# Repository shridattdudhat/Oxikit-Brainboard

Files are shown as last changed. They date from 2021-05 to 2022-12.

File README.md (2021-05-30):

# Oxikit-Brainboard

An Open Source Oxygen Concentrator Brain Board

Following are details of each directory:

- **BOM** : Bill Of Material for BrainBoard
- **Firmware** : Firmware to use with BrainBoard. It has two different firmware folder. 
  - Particle Electron Firmware
  - ESP32 TTGO T-Call firmware
- **gerberFiles** : You can download the zip and give for production.
- **images** : It has all the 3D images of BrainBoard
- **kicadProject** : It cotains all the files of Kicad Project. One can install latest Kicad nightly build and run the project to modify it. 
- **schematic** : Schematic file of the PCB

Some Kicad generated 3D images:

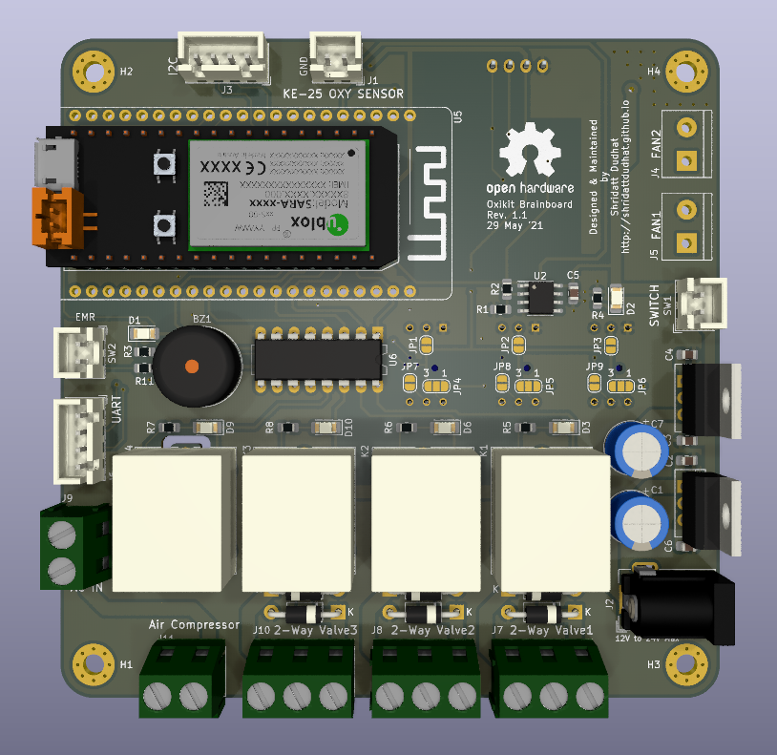
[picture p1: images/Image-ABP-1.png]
Front Side

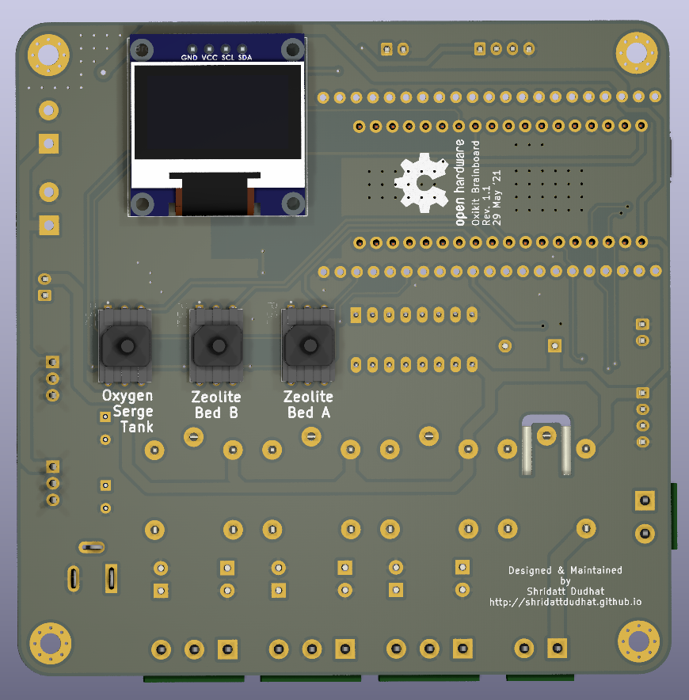
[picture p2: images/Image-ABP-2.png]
Back Side

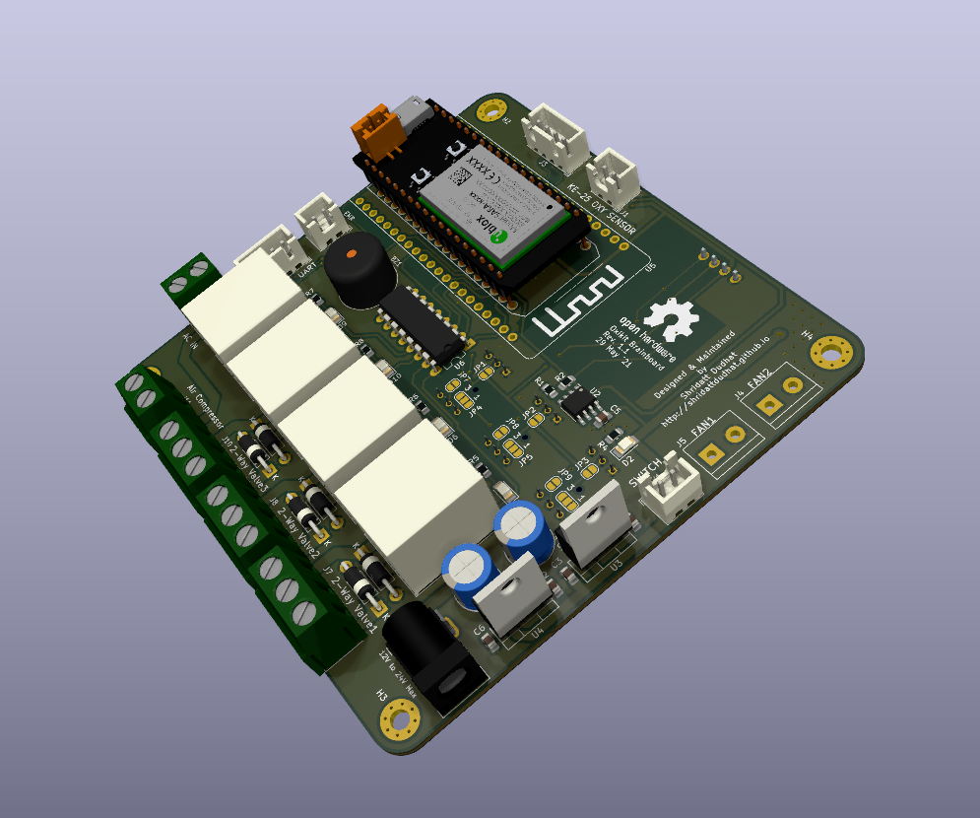
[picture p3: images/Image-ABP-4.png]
Side View


First prototypes of BrainBoard:

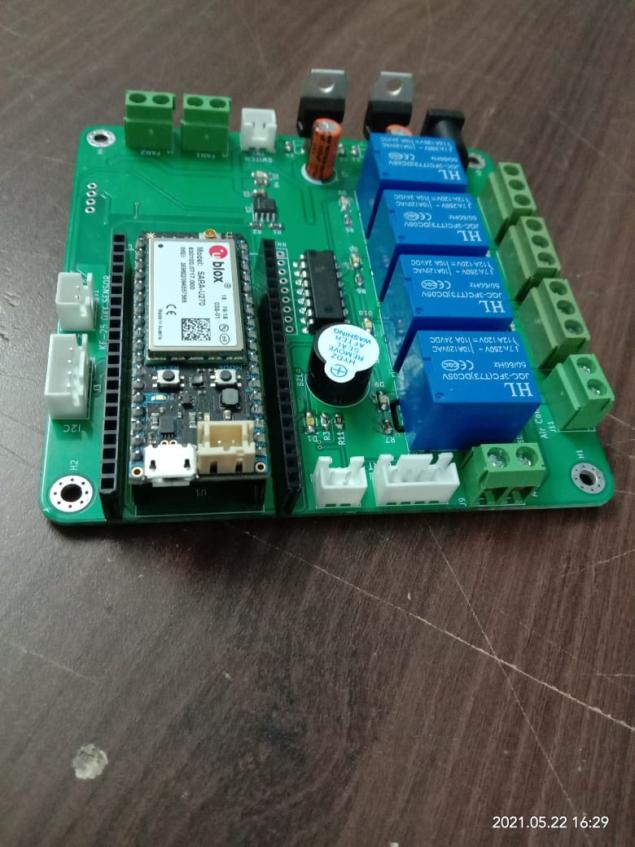
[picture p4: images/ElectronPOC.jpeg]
Particle electron

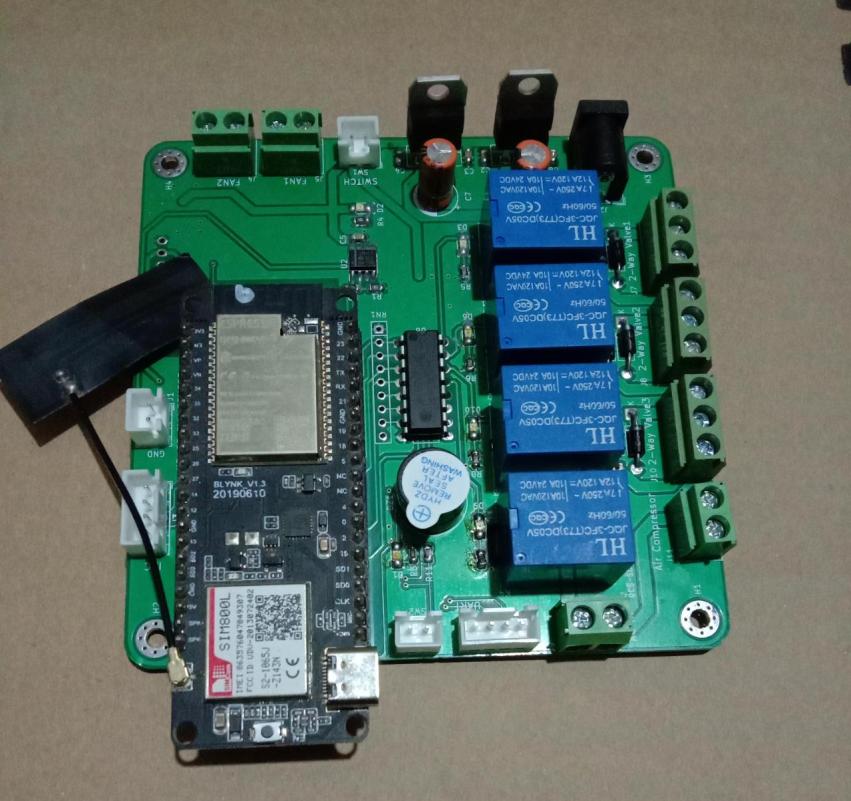
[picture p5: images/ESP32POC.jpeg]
EPS32


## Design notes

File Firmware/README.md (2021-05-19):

Will be uploading firmware for Electron and ESP32 soon.

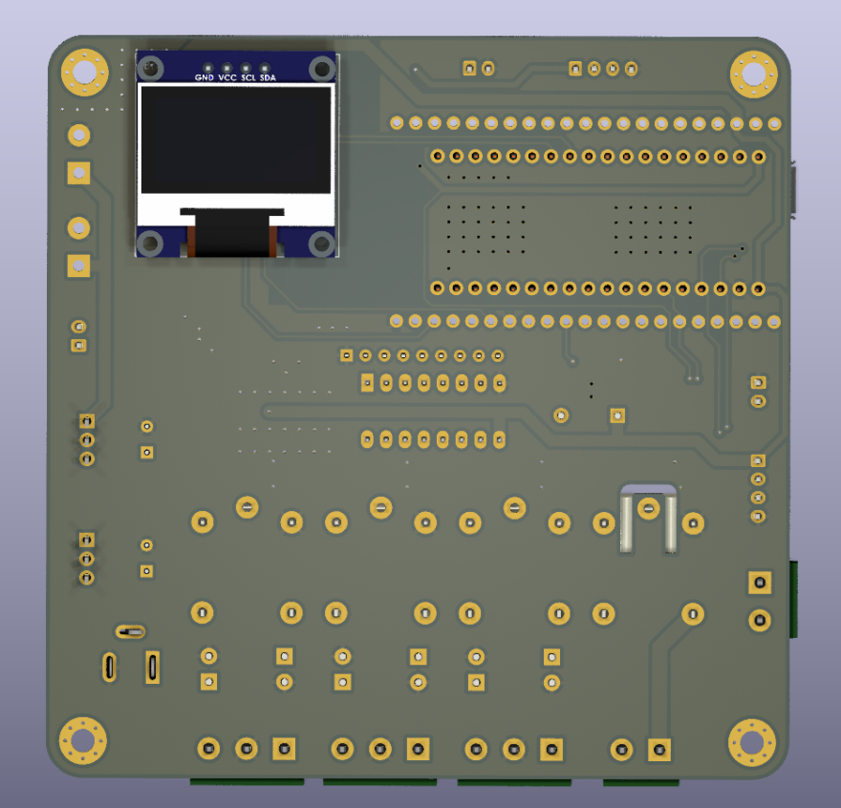
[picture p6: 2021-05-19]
images/back.png

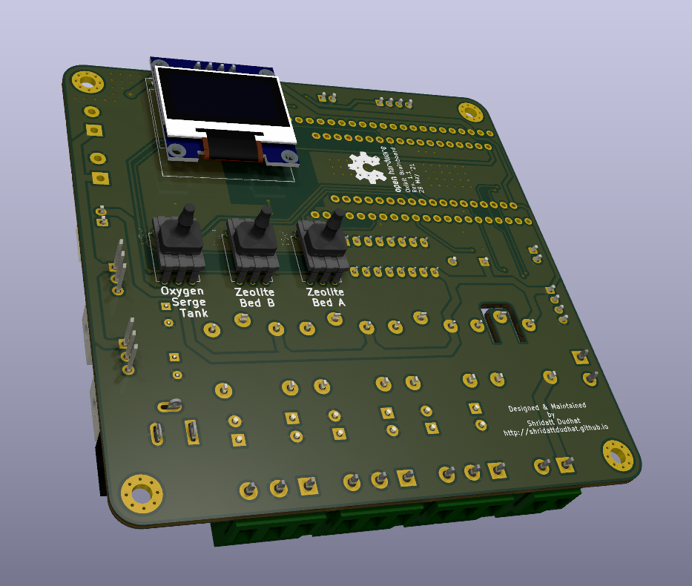
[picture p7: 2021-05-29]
images/Image-ABP-3.png

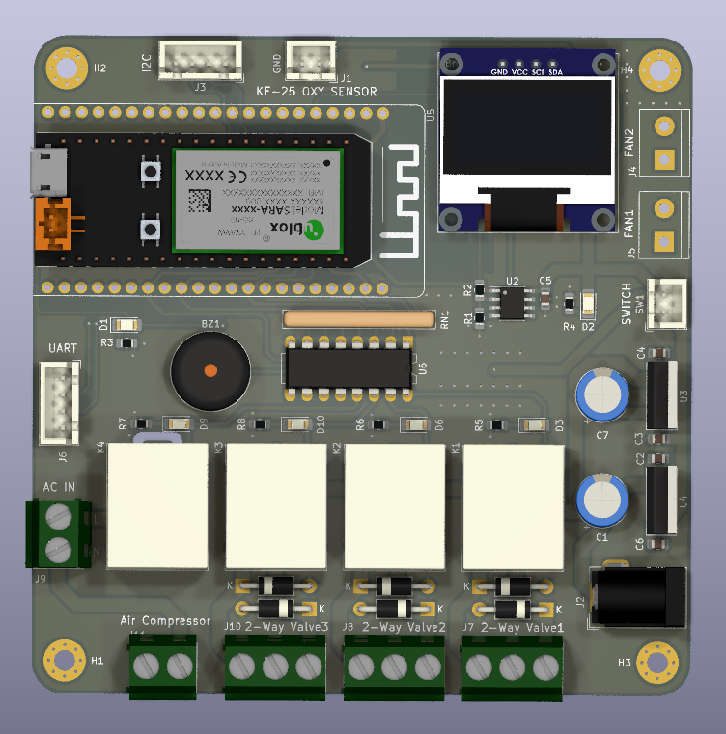
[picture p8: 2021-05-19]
images/front.png

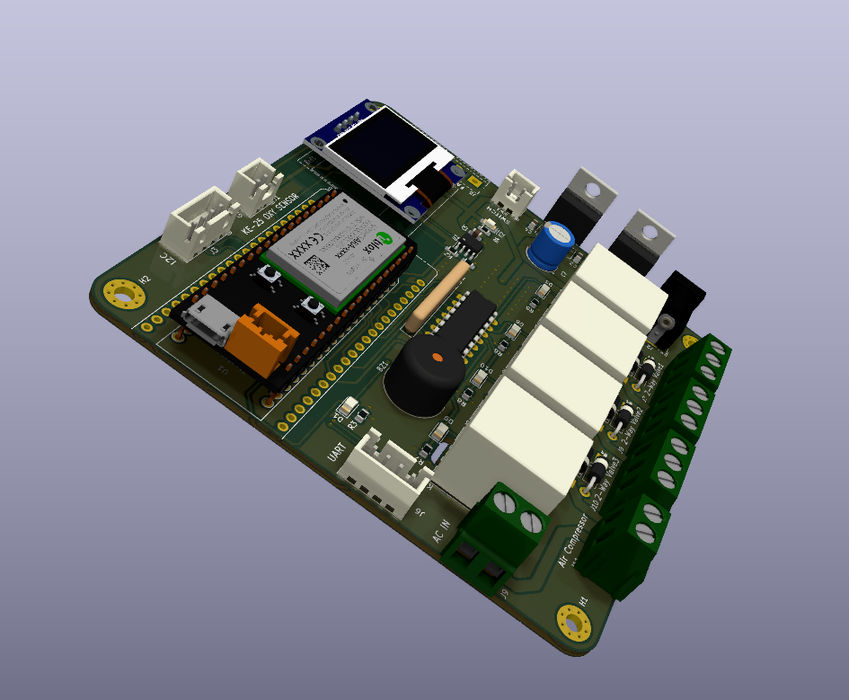
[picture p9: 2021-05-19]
images/sideView.png

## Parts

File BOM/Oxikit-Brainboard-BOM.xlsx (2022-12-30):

Sr. No. | Designator | Component value | Manufacturer Part Number | Qty per PCB | Package / Case | Per Component | Per PCB | Description | Ref Link (Local Purchase)
1 | Brd1 | SSD1306 | * | 1 | SSD1306:128x64OLED | 300 | 300 | I2C OLED Display | https://www.sunrobotics.in/shop/product/7375-oled-0-96-inch-i2c-display-module-4-pin-generic-3930
2 | BZ1 | Buzzer | * | 1 | Buzzer_Beeper:Buzzer_12x9.5RM7.6 | 15 | 15 | Electromagnetic Active Buzzer 5V | https://www.sunrom.com/p/electromagnetic-active-buzzer-5v
3 | C1, C7 | 220uF | MCGPR16V227M6.3X11 | 2 | Capacitor_THT:CP_Radial_D8.0mm_P3.50mm | 3 | 6 | Electrolytic Capacitor, 220 µF, 16 V, MCGPR Series, ± 20%, Radial Leaded, 2000 hours @ 85°C
4 | C2, C3, C4, C6 | 1uF | MC0805F105Z500CT | 4 | Capacitor_SMD:C_0805_2012Metric_Pad1.18x1.45mm_HandSolder | 2 | 8 | 1 µF, 50 V, 0805 [2012 Metric] | https://www.sunrom.com/p/1uf-105-0805-2012-metric
5 | C5 | 100nF | MC0805B104M500CT | 1 | Capacitor_SMD:C_0805_2012Metric_Pad1.18x1.45mm_HandSolder | 1 | 1 | 0.1 µF, 50 V, 0805 [2012 Metric], ± 20%, X7R | https://www.sunrom.com/p/100nf-104-0805-2012-metric
6 | D1, D2, D3, D6, D9, D10 | LED | * | 6 | LED_SMD:LED_1206_3216Metric_Pad1.42x1.75mm_HandSolder | 1 | 6 | Red SMD LED 1206 | https://www.sunrom.com/p/red-smd-led-1206
7 | D4, D5, D7, D8, D11, D12 | 1N4007 | 1N4007 | 6 | Diode_THT:D_DO-41_SOD81_P10.16mm_Horizontal | 1.5 | 9 | DIODE, STANDARD RECOVERY, 1A, 1KV, DO-41 | https://www.sunrom.com/p/1n4007-1a-diode
8 | J1 | OXY-Sensor | * | 1 | Connector_JST:JST_XH_B2B-XH-A_1x02_P2.50mm_Vertical | 1.5 | 1.5 | JST 2 Pin 2.54mm Pitch | https://www.sunrom.com/p/2-pin-jst-xh-25mm-top-entry-header
9 | J2 | Jack-DC | * | 1 | Connector_BarrelJack:BarrelJack_Wuerth_6941xx301002 | 13 | 13 | DC Socket - 1mm legs - Suitable for 5.5x2.1mm DC Pins | https://www.sunrom.com/p/dc-socket---1mm-legs---suitable-for-55x21mm-dc-pins
10 | J3, J6 | UART, I2C | * | 2 | Connector_JST:JST_XH_B4B-XH-A_1x04_P2.50mm_Vertical |  |  | 4 pin JST XH 2.5mm Top Entry Header | https://www.sunrom.com/p/4-pin-jst-xh-25mm-top-entry-header
11 | J4, J5, J9, J11 | Fan1 | * | 4 | TerminalBlock:TerminalBlock_bornier-2_P5.08mm | 7 | 28 | 2P 5mm 10A Screw Terminal Light | https://www.sunrom.com/p/2p-5mm-10a-screw-terminal-light
12 | J7, J8, J10 | Valve1 | * | 3 | TerminalBlock:TerminalBlock_bornier-3_P5.08mm | 11 | 33 | 3P 5mm 10A Screw Terminal Light | https://www.sunrom.com/p/3p-5mm-10a-screw-terminal-light
13 | K1, K2, K3, K4 | FINDER-36.11 | * | 4 | Relay_THT:Relay_SPDT_Finder_36.11 | 24 | 100 | Relay 5V - PCB Mount | https://www.sunrom.com/p/relay-5v-pcb-mount
14 | R1, R4, R5, R6, R7, R8, R9, R10, R11 | 1K | MCWR08X1001FTL | 9 | Resistor_SMD:R_0805_2012Metric_Pad1.20x1.40mm_HandSolder | 0.5 | 5 | 1 kohm, ± 1%, 125 mW, 0805 [2012 Metric] | https://www.sunrom.com/p/1k-1-0805-pack-of-100
15 | R2 | 10K | MCWR08X1002FTL | 1 | Resistor_SMD:R_0805_2012Metric_Pad1.20x1.40mm_HandSolder | 0.5 | 0.5 | 10 kohm, ± 1%, 125 mW, 0805 [2012 Metric] | https://www.sunrom.com/p/10k-1-0805-pack-of-100
16 | R3 | 330R | MCWR08X3300FTL | 1 | Resistor_SMD:R_0805_2012Metric_Pad1.20x1.40mm_HandSolder | 0.5 | 0.5 | 330 ohm, ± 1%, 125 mW, 0805 [2012 Metric] | https://www.sunrom.com/m/6867
18 | SW1, SW2 | Switch | * | 2 | Connector_JST:JST_XH_B2B-XH-A_1x02_P2.50mm_Vertical |  |  | JST 2 Pin 2.54mm Pitch | https://www.sunrom.com/p/2-pin-jst-xh-25mm-top-entry-header
19 | U1 | Electron |  | 1 | particle:electron
20 | U2 | LM358 | LM358EDR2G | 1 | Package_SO:SOIC-8_3.9x4.9mm_P1.27mm | 13 | 13 | Operational Amplifier, 2 Amplifier, 1 MHz, 0.6 V/µs, 3V to 32V, SOIC, 8 Pins
21 | U3, U4 | LM7805_TO220 | L7805CV | 2 | Package_TO_SOT_THT:TO-220-3_Vertical | 15 | 30 | Linear Voltage Regulator, 7805, Fixed, Positive, 10V To 35V In, 5V And 1.5A Out, TO-220-3
22 | U5 | TTGO-TCALL-SIM800 |  | 1 | TTGO-TCALL-SIM800:TTGO-TCALL-SIM800
23 | U6 | ULN2003A | ULN2003AN . | 1 | Package_DIP:DIP-16_W7.62mm_LongPads | 21 | 21 | Bipolar Transistor Array, NPN, 50 V, 500 mA, 25 W, 600 hFE, DIP | https://www.sunrom.com/p/uln2003a-dip
 |  |  | * Please Check links in last column

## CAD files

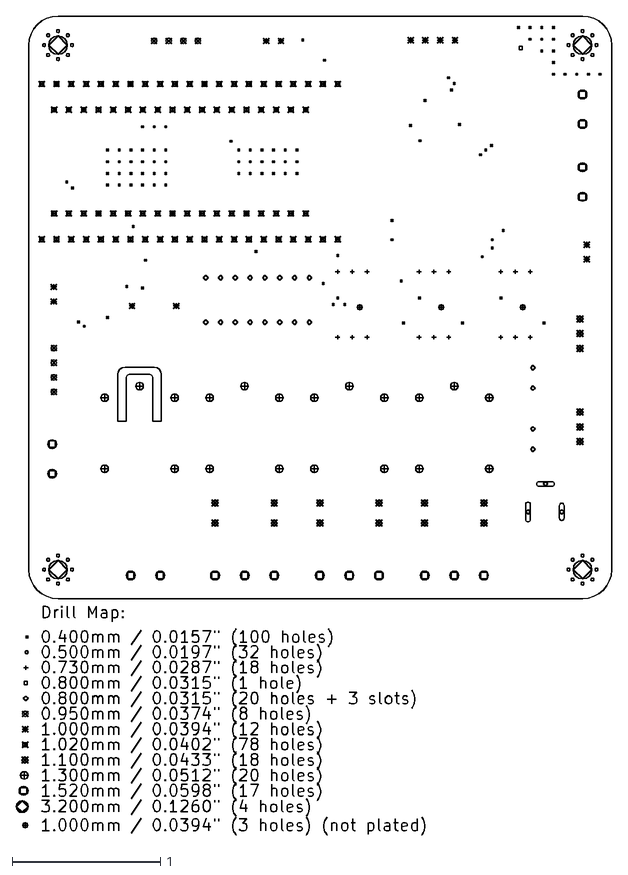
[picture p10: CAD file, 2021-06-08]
kicadProject/OxiKit-Brainboard_v1-GERBER/OxiKit-Brainboard_v1-drl_map.dxf
4.02 x 5.53

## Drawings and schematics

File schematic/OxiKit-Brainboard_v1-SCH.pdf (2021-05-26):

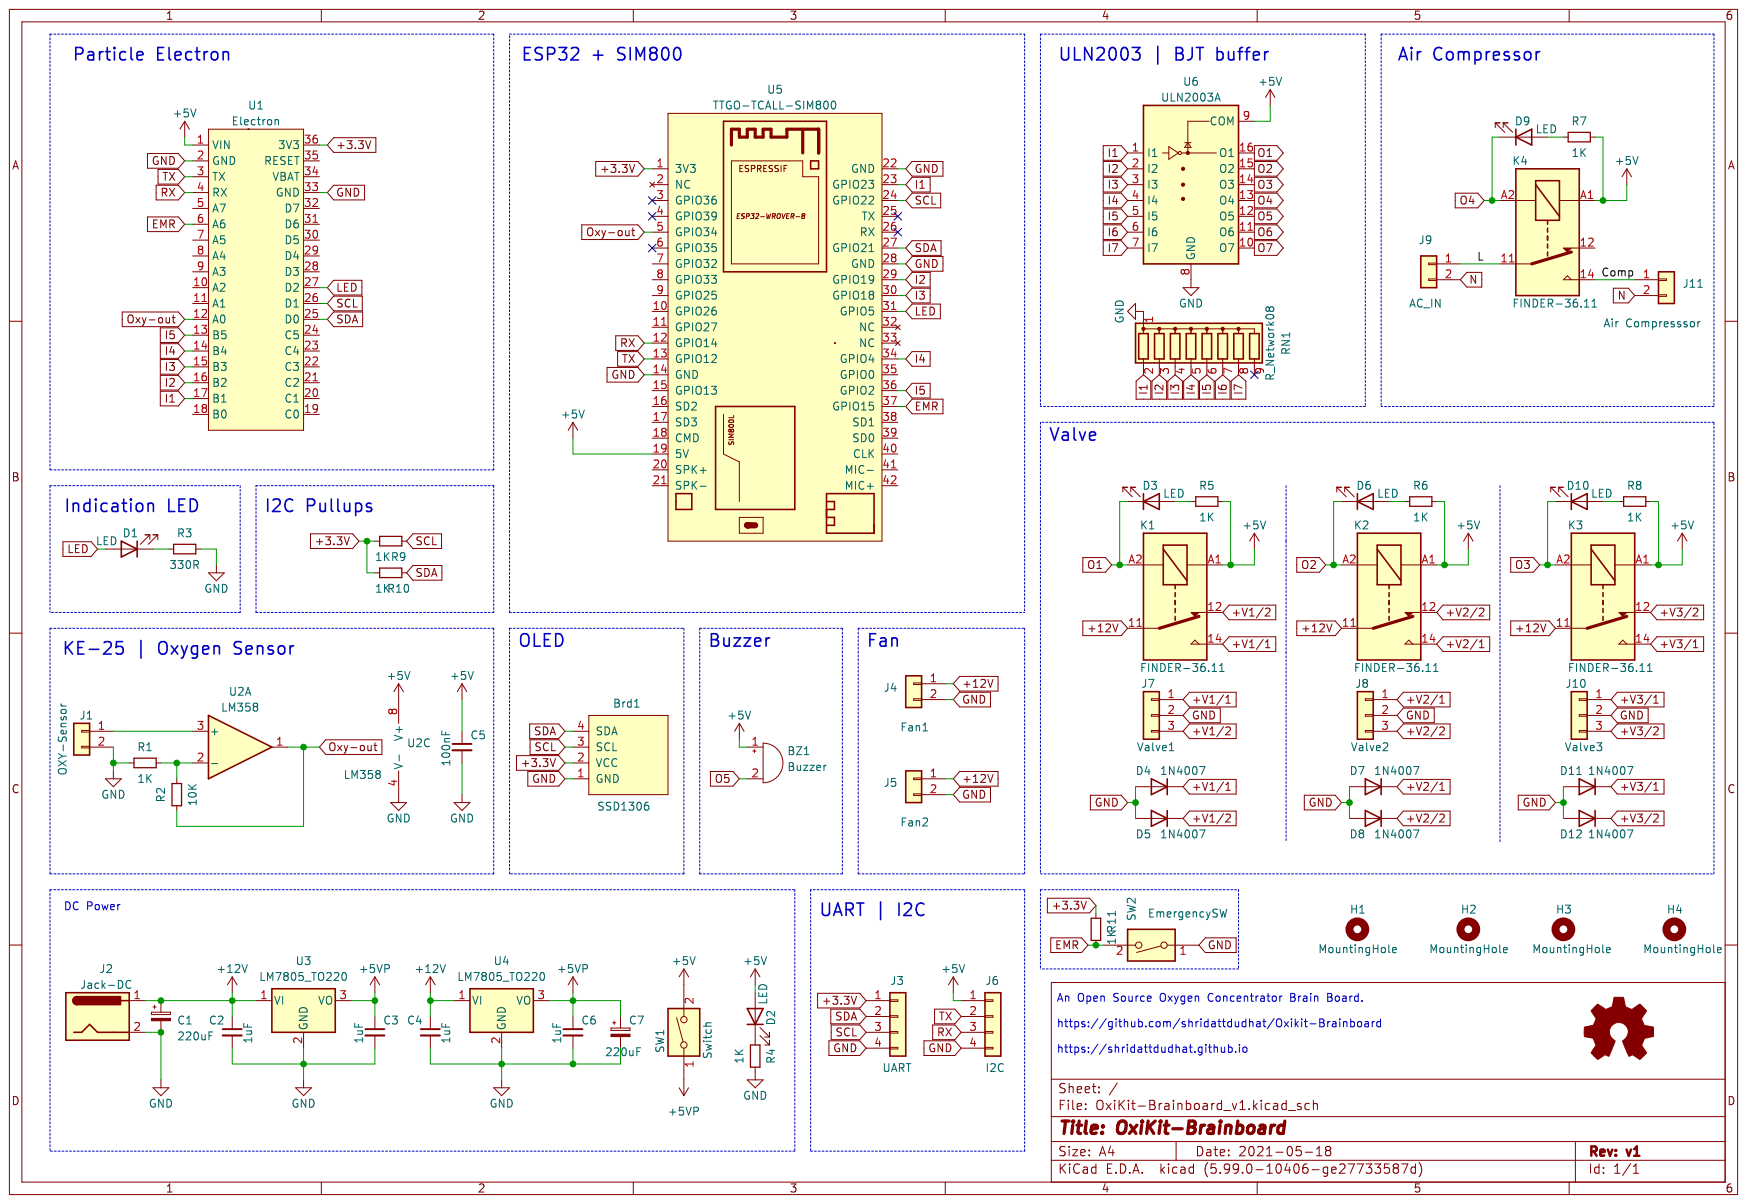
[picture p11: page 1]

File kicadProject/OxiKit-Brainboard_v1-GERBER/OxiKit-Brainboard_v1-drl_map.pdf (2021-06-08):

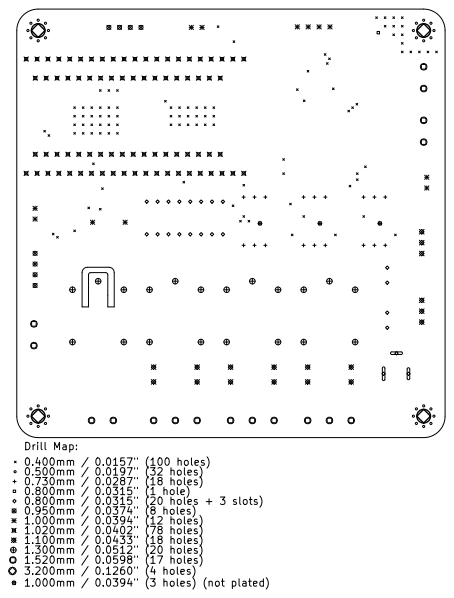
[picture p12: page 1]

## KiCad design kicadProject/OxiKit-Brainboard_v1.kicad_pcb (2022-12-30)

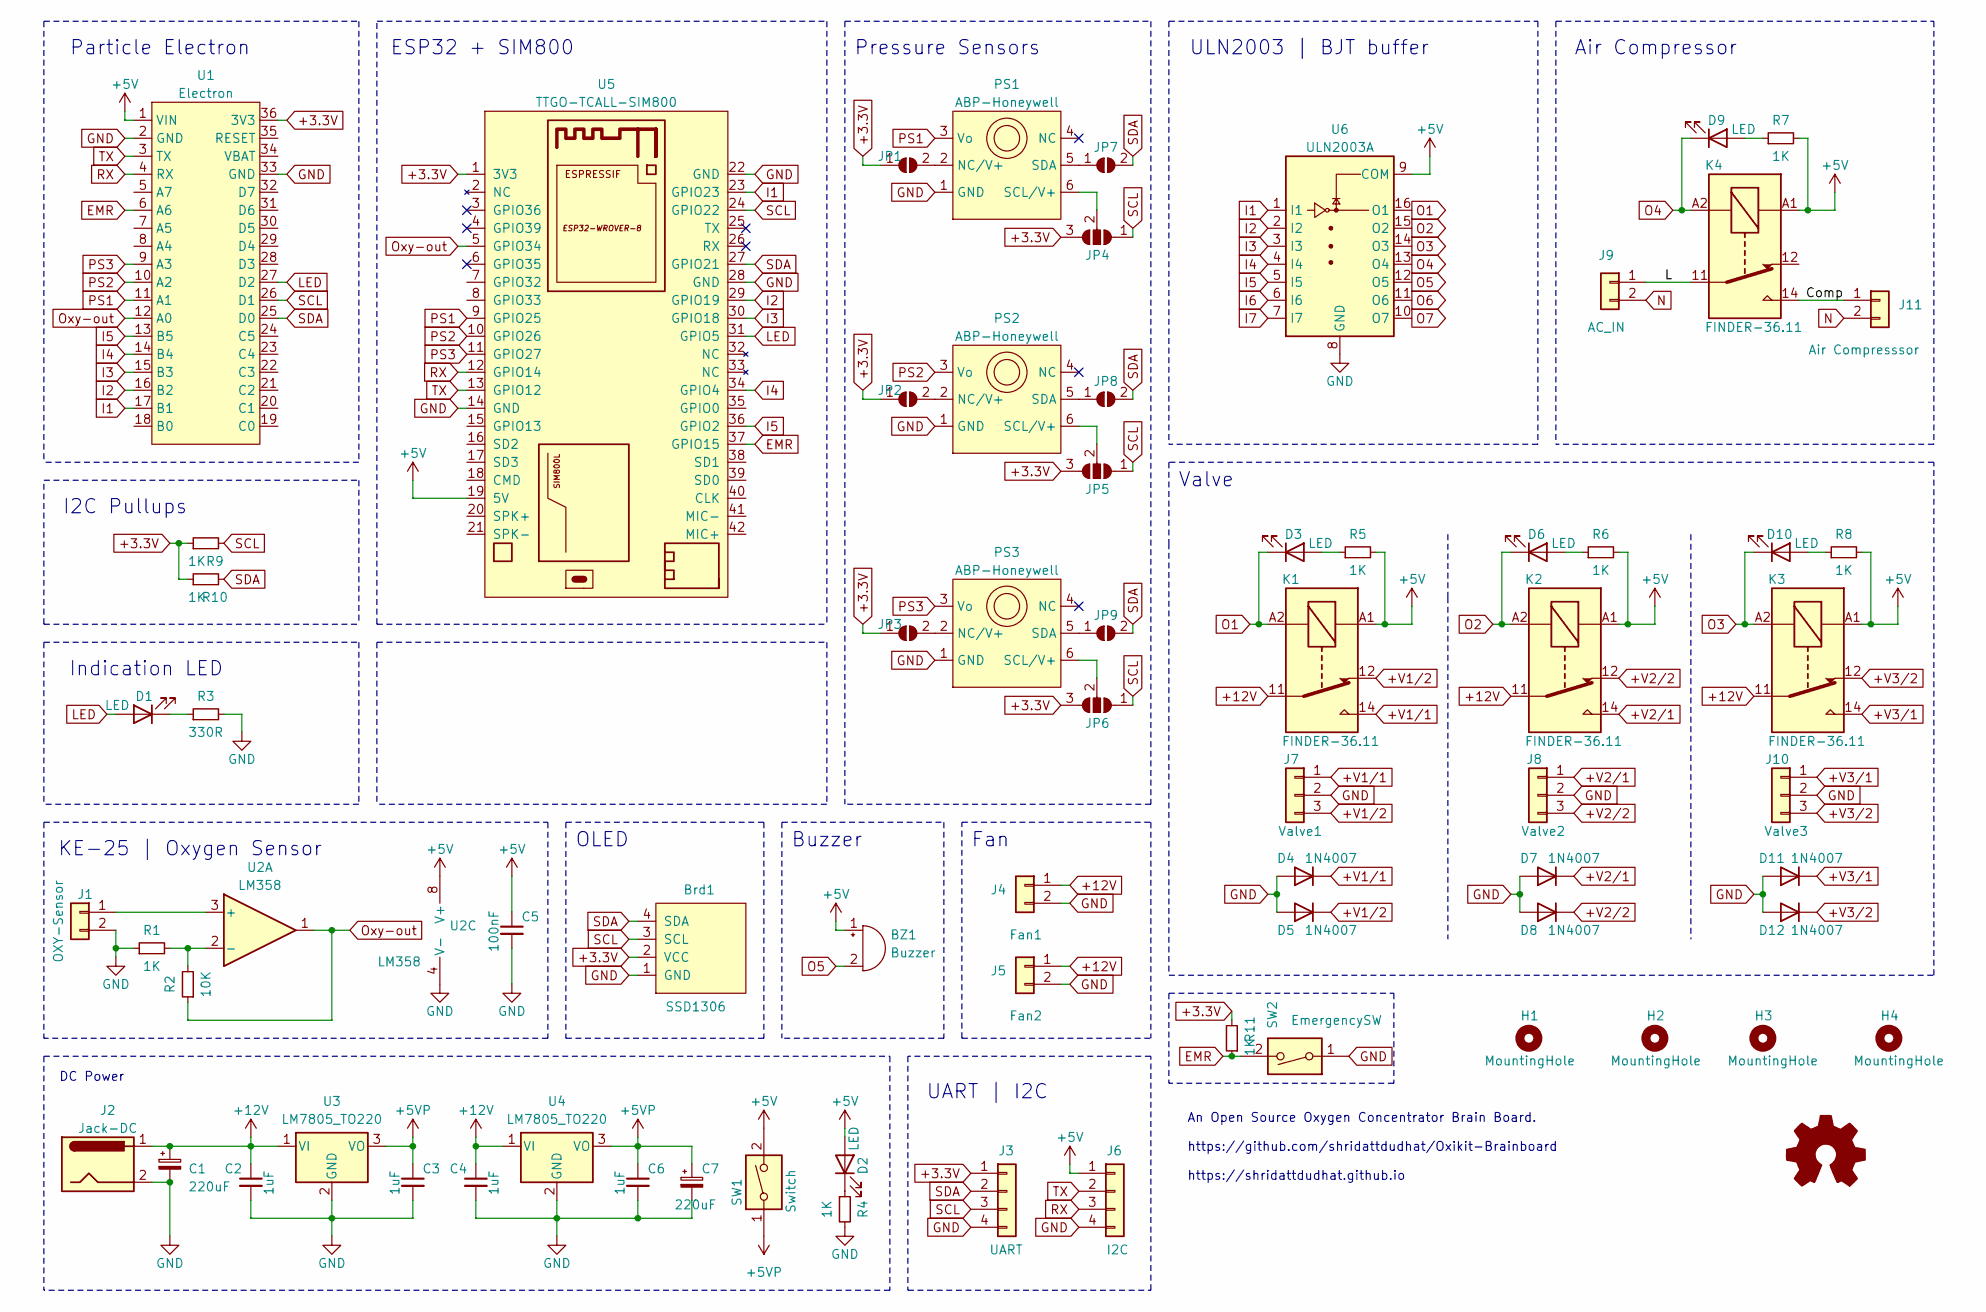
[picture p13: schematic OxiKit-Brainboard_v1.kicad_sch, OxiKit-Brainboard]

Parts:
BZ1: Buzzer; Buzzer_12x9.5RM7.6
Brd1: SSD1306; 128x64OLED
C1, C7: 220uF; CP_Radial_D8.0mm_P3.50mm
C2, C3, C4, C6: 1uF; C_0805_2012Metric_Pad1.18x1.45mm_HandSolder
C5: 100nF; C_0805_2012Metric_Pad1.18x1.45mm_HandSolder
D1, D2, D3, D6, D9, D10: LED; LED_1206_3216Metric_Pad1.42x1.75mm_HandSolder
D4, D5, D7, D8, D11, D12: 1N4007; D_DO-41_SOD81_P10.16mm_Horizontal
H1, H2, H3, H4: MountingHole; MountingHole_3.2mm_M3_Pad_Via
J1: OXY-Sensor; JST_XH_B2B-XH-A_1x02_P2.50mm_Vertical
J2: Jack-DC; BarrelJack_Wuerth_6941xx301002
J3: UART; JST_XH_B4B-XH-A_1x04_P2.50mm_Vertical
J4: Fan1; TerminalBlock_bornier-2_P5.08mm
J5: Fan2; TerminalBlock_bornier-2_P5.08mm
J6: I2C; JST_XH_B4B-XH-A_1x04_P2.50mm_Vertical
J7: Valve1; TerminalBlock_bornier-3_P5.08mm
J8: Valve2; TerminalBlock_bornier-3_P5.08mm
J9: AC_IN; TerminalBlock_bornier-2_P5.08mm
J10: Valve3; TerminalBlock_bornier-3_P5.08mm
J11: Air Compresssor; TerminalBlock_bornier-2_P5.08mm
JP1, JP2, JP3, JP7, JP8, JP9: SolderJumper_2_Open; SolderJumper-2_P1.3mm_Open_RoundedPad1.0x1.5mm
JP4, JP5, JP6: SolderJumper_3_Open; SolderJumper-3_P1.3mm_Open_RoundedPad1.0x1.5mm_NumberLabels
K1, K2, K3, K4: FINDER-36.11; Relay_SPDT_Finder_36.11
PS1, PS2, PS3: ABP-Honeywell; ABP-Series-Pressure
R1, R4, R5, R6, R7, R8, R9, R10, R11: 1K; R_0805_2012Metric_Pad1.20x1.40mm_HandSolder
R2: 10K; R_0805_2012Metric_Pad1.20x1.40mm_HandSolder
R3: 330R; R_0805_2012Metric_Pad1.20x1.40mm_HandSolder
SW1: Switch; JST_XH_B2B-XH-A_1x02_P2.50mm_Vertical
SW2: EmergencySW; JST_XH_B2B-XH-A_1x02_P2.50mm_Vertical
U1: Electron; electron
U2: LM358
U3, U4: LM7805_TO220; TO-220-3_Vertical
U5: TTGO-TCALL-SIM800
U6: ULN2003A; DIP-16_W7.62mm_LongPads

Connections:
+3.3V: Brd1.2 (VCC), J3.1, JP1.1 (A), JP2.1 (A), JP3.1 (A), JP4.3 (B), JP5.3 (B), JP6.3 (B), R9.1, R10.1, R11.2, U1.36 (3V3), U5.1 (3V3)
+5V: BZ1.1 (-), C5.1, D2.2 (A), J6.1, K1.A1, K2.A1, K3.A1, K4.A1, R5.2, R6.2, R7.2, R8.2, SW1.2, U1.1 (VIN), U2.8 (V+), U5.19 (5V), U6.9 (COM)
+5VP: C3.1, C6.1, C7.1, SW1.1, U3.3 (VO), U4.3 (VO)
+12V: C1.1, C2.1, C4.1, J2.1, J4.1, J5.1, K1.11, K2.11, K3.11, U3.1 (VI), U4.1 (VI)
+V1/1: D4.1 (K), J7.1, K1.14
+V1/2: D5.1 (K), J7.3, K1.12
+V2/1: D7.1 (K), J8.1, K2.14
+V2/2: D8.1 (K), J8.3, K2.12
+V3/1: D11.1 (K), J10.1, K3.14
+V3/2: D12.1 (K), J10.3, K3.12
/Comp: J11.1, K4.14
/L: J9.1, K4.11
EMR: R11.1, SW2.2, U1.6 (A6), U5.37 (GPIO15)
GND: Brd1.1 (GND), C1.2, C2.2, C3.2, C4.2, C5.2, C6.2, C7.2, D4.2 (A), D5.2 (A), D7.2 (A), D8.2 (A), D11.2 (A), D12.2 (A), J1.2, J2.2, J3.4, J4.2, J5.2, J6.4, J7.2, J8.2, J10.2, PS1.1 (GND), PS2.1 (GND), PS3.1 (GND), R1.1, R3.2, R4.2, SW2.1, U1.2 (GND), U1.33 (GND), U2.4 (V-), U3.2 (GND), U4.2 (GND), U5.14 (GND), U5.22 (GND), U5.28 (GND), U6.8 (GND)
I1: U1.17 (B1), U5.23 (GPIO23), U6.1 (I1)
I2: U1.16 (B2), U5.29 (GPIO19), U6.2 (I2)
I3: U1.15 (B3), U5.30 (GPIO18), U6.3 (I3)
I4: U1.14 (B4), U5.34 (GPIO4), U6.4 (I4)
I5: U1.13 (B5), U5.36 (GPIO2), U6.5 (I5)
I6: U6.6 (I6)
I7: U6.7 (I7)
LED: D1.2 (A), U1.27 (D2), U5.31 (GPIO5)
N: J9.2, J11.2
unnamed: D1.1 (K), R3.1
unnamed: D2.1 (K), R4.1
unnamed: D3.2 (A), R5.1
unnamed: D6.2 (A), R6.1
unnamed: D9.2 (A), R7.1
unnamed: D10.2 (A), R8.1
unnamed: J1.1, U2.3 (+)
unnamed: JP1.2 (B), PS1.2 (NC/V+)
unnamed: JP2.2 (B), PS2.2 (NC/V+)
unnamed: JP3.2 (B), PS3.2 (NC/V+)
unnamed: JP4.2 (C), PS1.6 (SCL/V+)
unnamed: JP5.2 (C), PS2.6 (SCL/V+)
unnamed: JP6.2 (C), PS3.6 (SCL/V+)
unnamed: JP7.1 (A), PS1.5 (SDA)
unnamed: JP8.1 (A), PS2.5 (SDA)
unnamed: JP9.1 (A), PS3.5 (SDA)
unnamed: R1.2, R2.2, U2.2 (-)
O1: D3.1 (K), K1.A2, U6.16 (O1)
O2: D6.1 (K), K2.A2, U6.15 (O2)
O3: D10.1 (K), K3.A2, U6.14 (O3)
O4: D9.1 (K), K4.A2, U6.13 (O4)
O5: BZ1.2 (+), U6.12 (O5)
O6: U6.11 (O6)
O7: U6.10 (O7)
Oxy-out: R2.1, U1.12 (A0), U2.1, U5.5 (GPIO34)
PS1: PS1.3 (Vo), U1.11 (A1), U5.9 (GPIO25)
PS2: PS2.3 (Vo), U1.10 (A2), U5.10 (GPIO26)
PS3: PS3.3 (Vo), U1.9 (A3), U5.11 (GPIO27)
RX: J6.3, U1.4 (RX), U5.12 (GPIO14)
SCL: Brd1.3 (SCL), J3.3, JP4.1 (A), JP5.1 (A), JP6.1 (A), R9.2, U1.26 (D1), U5.24 (GPIO22)
SDA: Brd1.4 (SDA), J3.2, JP7.2 (B), JP8.2 (B), JP9.2 (B), R10.2, U1.25 (D0), U5.27 (GPIO21)
TX: J6.2, U1.3 (TX), U5.13 (GPIO12)

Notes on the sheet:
DC Power
I2C Pullups
Indication LED
Particle Electron
KE-25 | Oxygen Sensor
ESP32 + SIM800
OLED
Buzzer
Pressure Sensors
UART | I2C
Fan
Valve
An Open Source Oxygen Concentrator Brain Board. https://github.com/shridattdudhat/Oxikit-Brainboard https://shridattdudhat.github.io
ULN2003 | BJT buffer
Air Compressor

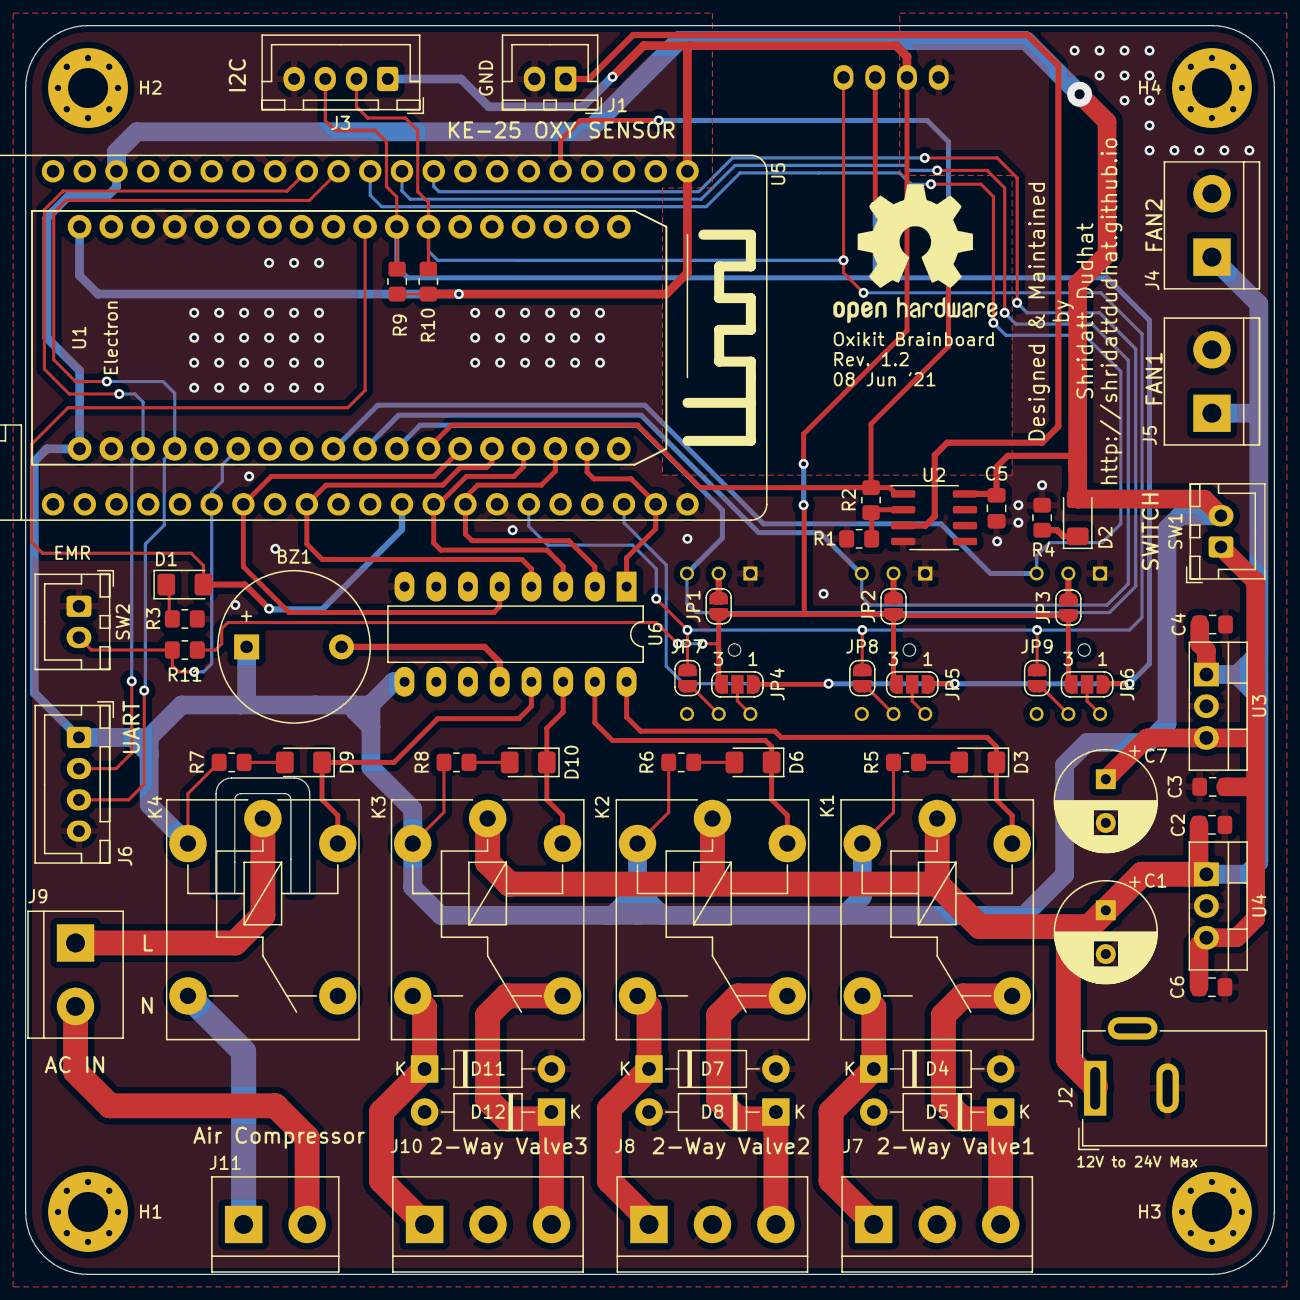
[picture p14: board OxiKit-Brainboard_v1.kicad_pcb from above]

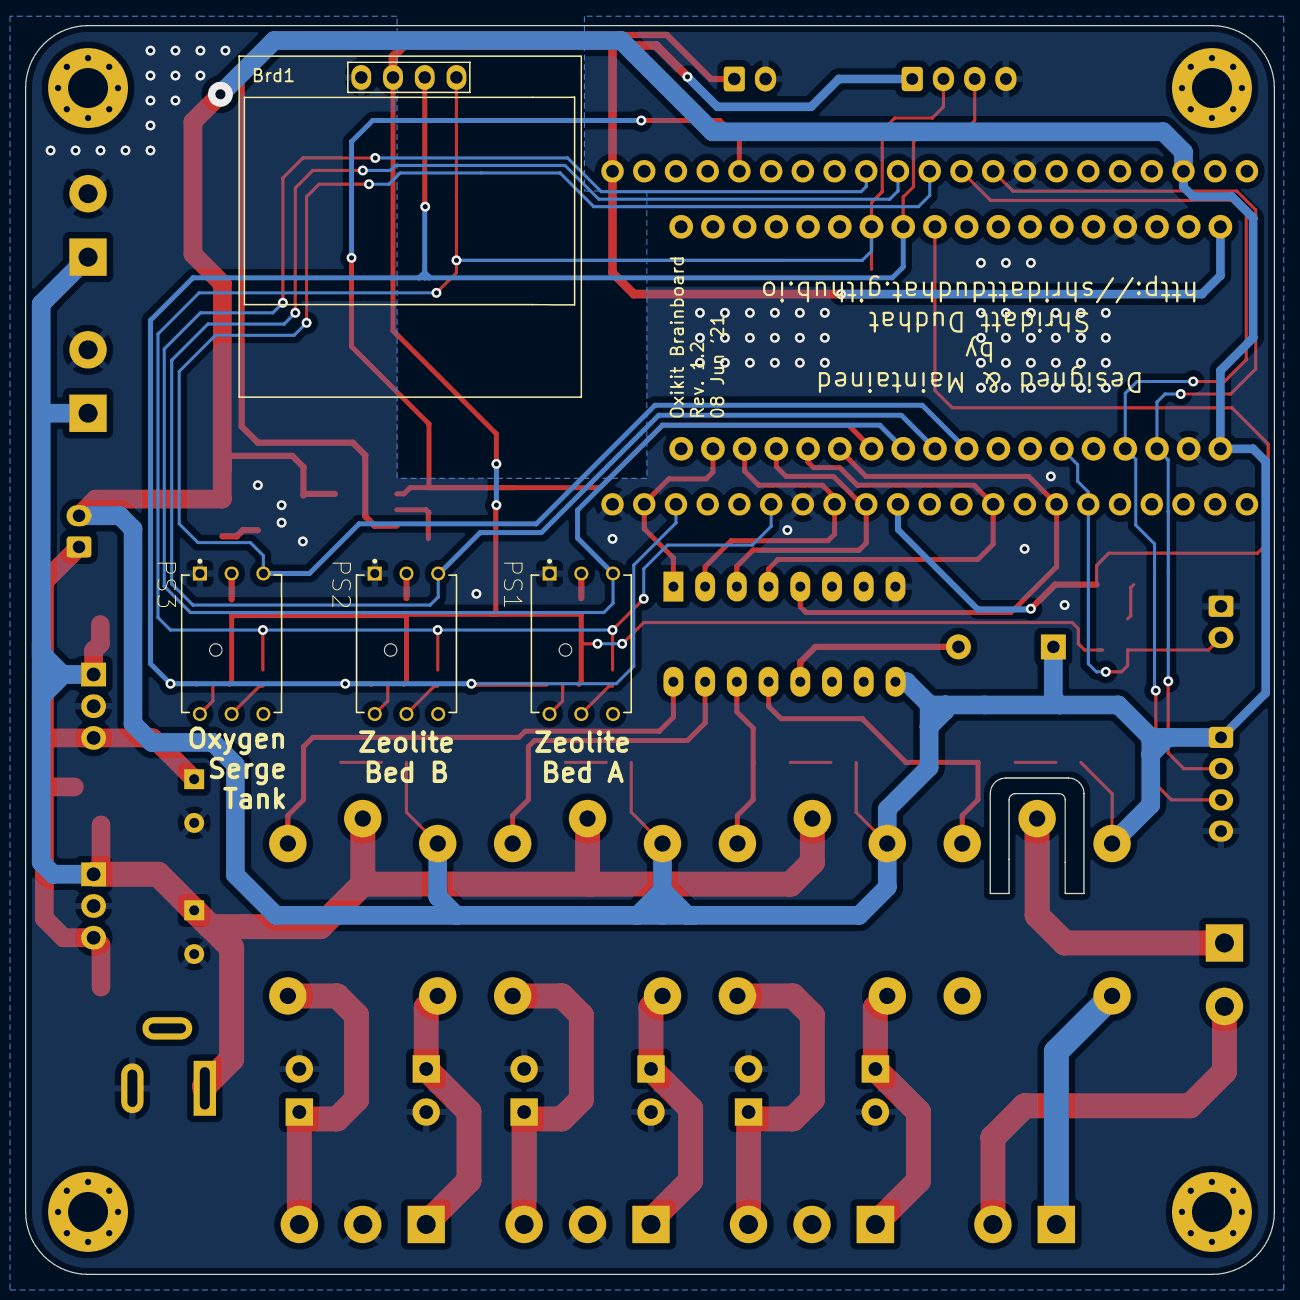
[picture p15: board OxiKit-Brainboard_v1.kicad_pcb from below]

Board: 2 copper layers, 100.0 x 100.0 mm, 71 parts (4 on the bottom side), 51 nets.

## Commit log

2021-05-18 Initial Schematic Commit | Relays, Buzzer, OxySensor, Power Supply, OLED
    [OxiKit-Brainboard_v1.kicad_pcb, OxiKit-Brainboard_v1.kicad_sch]
2021-05-19 Component Placement - L1
    [OxiKit-Brainboard_v1.kicad_pcb, OxiKit-Brainboard_v1.kicad_sch]
2021-05-19 Final routing
    [OxiKit-Brainboard_v1-B_Cu.gbr, OxiKit-Brainboard_v1-B_Mask.gbr, OxiKit-Brainboard_v1-B_Paste.gbr, OxiKit-Brainboard_v1-B_Silkscreen.gbr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]
2021-05-19 Folder system updated
    [OxiKit-Brainboard_v1-B_Cu.gbr, OxiKit-Brainboard_v1-B_Mask.gbr, OxiKit-Brainboard_v1-B_Paste.gbr, OxiKit-Brainboard_v1-B_Silkscreen.gbr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]
2021-05-26 #1 ULN2003 and Relay connection Fixed, Indication LED of Relay also updated
    [OxiKit-Brainboard_v1.kicad_pcb, OxiKit-Brainboard_v1.kicad_sch]
2021-05-26 OSHW Logo Added
    [OxiKit-Brainboard_v1.kicad_pcb, OxiKit-Brainboard_v1.kicad_sch]
2021-05-26 New Gerber Files | #1 Fixed
    [OxiKit-Brainboard_v1-B_Cu.gbr, OxiKit-Brainboard_v1-B_Mask.gbr, OxiKit-Brainboard_v1-B_Paste.gbr, OxiKit-Brainboard_v1-B_Silkscreen.gbr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]
2021-05-29 ABP Honeywell Pressure Sensor added
    [OxiKit-Brainboard_v1-B_Cu.gbr, OxiKit-Brainboard_v1-B_Mask.gbr, OxiKit-Brainboard_v1-B_Paste.gbr, OxiKit-Brainboard_v1-B_Silkscreen.gbr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]
2021-05-29 New Gerber added with DIP Pressure Sensor
2021-06-08 Pressure Sensor connection to ESP32 #2
    PS1 >> IO25
    PS2 >> IO26
    PS3 >> IO27
    [OxiKit-Brainboard_v1-B_Cu.gbr, OxiKit-Brainboard_v1-B_Mask.gbr, OxiKit-Brainboard_v1-B_Paste.gbr, OxiKit-Brainboard_v1-B_Silkscreen.gbr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]
